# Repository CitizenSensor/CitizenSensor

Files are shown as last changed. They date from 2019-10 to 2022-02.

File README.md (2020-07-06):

# CitizenSensor Nitrate Measurement System

CitizenSensor Nitrate Measurement System

This repository contains all design files for the CitizenSensor nitrate measuring system.

## Repository Layout

```
+ 1_RaspberryPi-HAT/            Raspberry Pi HAT allowing electro-chemical measurements
| + Firmware/                   firmware for the ADuCM350 on the HAT
| + Hardware/                   PCB design files for the HAT
+ 2_Software/                   Main software running on the Raspberry Pi
+ 3_Electrometer/               PCB design files for the electrometer amplifier
+ 4_ConnectorBoard/             PCB design files for a small board to connect further components
+ 5_Enclosure/                  3D printable enclosure
+ 6_Accessories/                Additional helpful items
+ README.md                     this readme
```

## Documentation

Documentation can be found in the [CitizenSensor Wiki](https://github.com/CitizenSensor/CitizenSensor/wiki)

## Known Issues

See [Open Issues](https://github.com/CitizenSensor/CitizenSensor/issues?utf8=%E2%9C%93&q=is%3Aopen+is%3Aissue).

## License

The hardware documentation is licensed under CERN OHL v.1.2.

Software is licensed under GPLv3.

For details see licensing info in the respective sub directories.

---

Copyright FabLab München e.V. and Fraunhofer EMFT 2019-2020

CitizenSensor is sponsored by the Federal Ministry of Education and Research

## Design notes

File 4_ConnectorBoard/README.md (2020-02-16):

# Connector Board

The connector board is a small PCB that sits on top of the CitizenSensor Raspberry Pi HAT and connects additional components to the Raspberry Pi, namely:

* HX711 breakout board to connect the load cell
* KY040 rotary encoder
* Motor for the magnetic stirrer

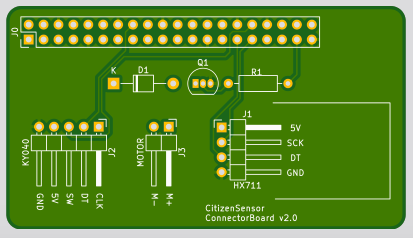
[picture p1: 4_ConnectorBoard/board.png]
PCB


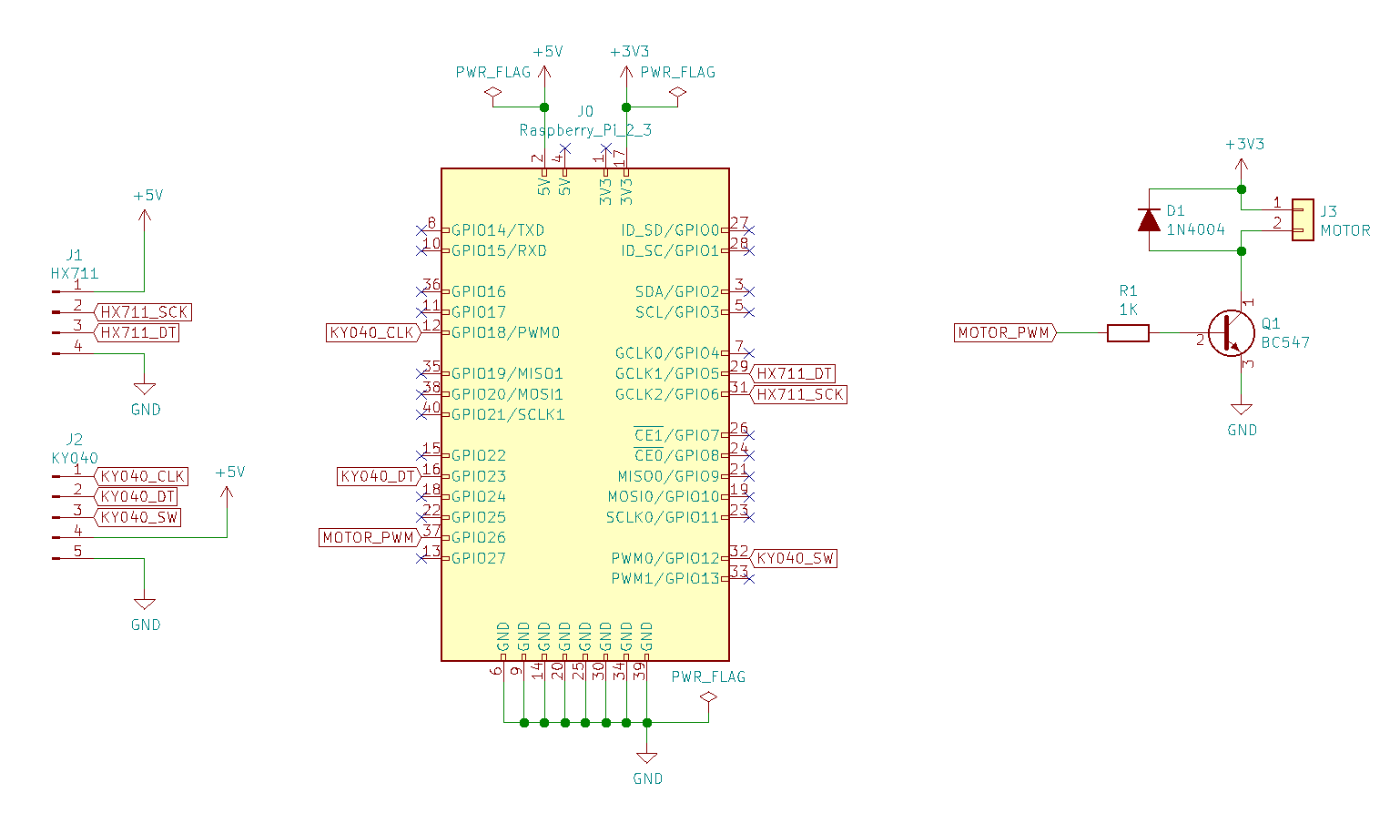
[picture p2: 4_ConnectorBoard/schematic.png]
Schematic


## Bill of Material

| Item | Description | Amount | Comment  |
| --- | --- | ---| ---  |
| J0 | Raspberry Pi Connector | 1 | 40 pins |
| J1 | Pin Header 90° 1x4 | 1 | 2.54 mm raster |
| J2 | Pin Header 90° 1x5 | 1 | 2.54 mm raster |
| J3 | Pin Header 90° 1x2 | 1 | 2.54 mm raster |
| R1 | 1K resistor | 1 | |
| D1 | 1N4004 diode| 1 | |
| Q1 | BC547| 1 | |

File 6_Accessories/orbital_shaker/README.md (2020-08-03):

# CitizenSensor Orbital Shaker

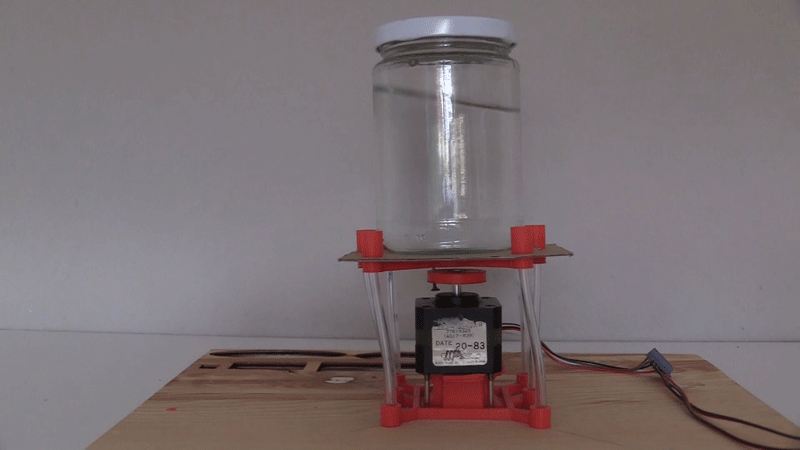
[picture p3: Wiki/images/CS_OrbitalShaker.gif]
CitizenSensor Orbital Shaker


The CitizenSensor Orbital Shaker is an Open Source device for shaking fluids.
This device was designed for for step ["Creation of Aqueous Solution"](https://github.com/CitizenSensor/CitizenSensor/blob/master/Wiki/CS_Usage_AqueousSolution.md), where an aqueous solution
is created by dissolving a soil sample in water. 

The design of the CitizenSensor Orbital Shaker has the following objectives:
- Construction based on few and simple components
- Support of sufficient load capacity (filled jam jar with a total weight of 450g)
- Robust mechanics for mixing the aqueous solution over a time period of 2 hours

## Assembly Instructions

1. Print the 3D Parts P1 - P3 (Recommended print parameters: 3 Shells, Infill 90%)
2. Sand the inner side of the circular ring of part P2 to reduce friction of the rotating nail
3. Place the stepper motor on a wood panel (at least 10 cm x 10 cm) and mark the locations of the holes in the stepper motor.
4. Drill the holes for fastening the stepper motor. Us a drill with a diameter that matches the screws for the stepper motor S1.
5. Place the Orbital Shaker Base P1 on the wood panel and put the Stepper Motor M1 on top.
6. Fasten the stepper motor M1 with the four screws S1.
7. Screw the clamping ring R1 tight on the stepper motor axis
8. Drill a little hole into the Orbital Shaker Rotating Disc - just as big that the thin nail N1 has a tight fits 
9. Mount the Orbital Shaker Rotating Disc on the clamping ring R1
10. Twist the six thin tubes in the holes of the shaker base 
11. Mount the Orbital Shaker Top: twist in the six thin tubes in the holes of the shaker top
12. Place the Orbital Shaker Platform P4 on the Orbital Shaker Top P2.
13. Connect the stepper motor to the stepper motor driver
14. Connect the stepper motor to the 12V power source
15. Connect the Arduino to the 5V power source
The Orbital Shaker Rotating Disc should now move the Orbital Shaker Top.
16. Disconnect the Arduino from the power source
17. Put the jam jar on the Orbital Shaker Platform, then reconnect the Arduino to the power source. The Orbital Shaker should now shake the jam jar.

In case the mechanics does not properly move, re-check that all tubes properly fit in the Orbital Shaker Base and Top. Also the Orbital Shaker Top might need smoe more sanding. 

## Bill of Material

| Item | Description | Amount | Comment  |
| --- | --- | ---| ---  |
| P1 | Orbital Shaker Base | 1 | 3D Print |
| P2 | Orbital Shaker Top | 1 | 3D Print |
| P3 | Orbital Shaker Rotating Disc | 1 | 3D Print |
| P4 | Orbital Shaker Platform | 1 | Lasercut |
| M1 | Stepper Motor | 1 | |
| R1 | Clamping Ring | 1 | Inside diameter must correspond to stepper motor axis |
| S1-S4 | Screws for Stepper Motor | 4 | |
| A1 | Arduino | 1 | |
| C1 | Stepper Motor Driver | 1 | |
| PS1 | Power Supply 12V | 1 | |
| PS2 | Power Supply 5V | 1 | |
| C1 | USB Cable | 1 | |
| T1-T6 | Thin Tube | 6 | Length: 82 mm, Outside Diameter 5mm |
| N1 | Thin Nail | 1 | |

## Credits

The CitizenSensor Orbital Shaker was inspired by the following projects:

* [Hackteria Orbital Shaker](https://www.hackteria.org/wiki/Orbital_Shaker)
* [Open Source Orbital Shaker by jmil (Thingiverse)](https://www.thingiverse.com/thing:5045)
* [DIYbio Orbital Shaker V 1.0 by ProgressTH (Thingiverse)](https://www.thingiverse.com/thing:2633507)
* [Crickit Lab Shaker by Ruiz Brothers (Adafruit)](https://learn.adafruit.com/crickit-lab-shaker/)

## License

Copyright FabLab Muenchen e.V. and Fraunhofer EMFT 2019.

This documentation describes Open Hardware and is licensed under the CERN OHL v. 1.2.

You may redistribute and modify this documentation under the terms of the CERN OHL v.1.2. 
(http://ohwr.org/cernohl). This documentation is distributed WITHOUT ANY EXPRESS OR 
IMPLIED WARRANTY, INCLUDING OF MERCHANTABILITY, SATISFACTORY QUALITY AND FITNESS FOR A 
PARTICULAR PURPOSE. 

Please see the CERN OHL v.1.2 for applicable conditions.

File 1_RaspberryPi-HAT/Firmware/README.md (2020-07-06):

# ADuCM350 Firmware for the Citizensensor project
> Code created by Matthias Steinmaßl

The Pi HAT equippes a M350 from Analog Devices. The Firmware can be compiled using IAR EWARM.

## Functions

It integrates readout of internal ADCs, basic communication functions with UART and BME680 (not tested).

Make sure that in the file `C:\Analog Devices\ADuCM350BBCZ\Eval-ADUCM350EBZ\inc\config\adi_i2c_config.h`
the settings are:
```
#define ADI_I2C_CFG_ENABLE_DMA_SUPPORT                     0
#define ADI_I2C_CFG_SLAVE_MODE_SUPPORT                     0
#define ADI_I2C_CFG_ENABLE_STATIC_CONFIG_SUPPORT           1
#define ADI_I2C_CFG_ENABLE_CALLBACK_SUPPORT                0
```

Open this directory: `C:\Analog Devices\ADuCM350BBCZ\` and clone the CitizenSensor repository here:
`git clone https://github.com/CitizenSensor/CitizenSensor`.

Open `C:\Analog Devices\ADuCM350BBCZ\CitizenSensor\1_RaspberryPi-HAT\Firmware\iar\Chronopotentiometrie.c`
with the IAR EWARM code-size limited IDE ([Link](https://www.iar.com/iar-embedded-workbench/#!?architecture=Arm)) and try to make it.

If it fails, check the following settings:
1. Project-Options-Build Actions: Correct path to ielftool.exe
2. Project-Options-C/C++ Compiler/Preprocessor: Check the correct paths to */examples, */inc and */inc/config
3. Check if all the files in Driver, System and Test Sources can be found, and if not re-add them.

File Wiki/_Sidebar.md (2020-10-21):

Überblick
* [CitizenSensor Überblick](https://github.com/CitizenSensor/CitizenSensor/wiki/Home-DE) 

Dokumentation
* [CitizenSensor Montage](https://github.com/CitizenSensor/CitizenSensor/blob/master/Wiki/CS_Assembly-DE.md)
* [CitizenSensor Bedienung](https://github.com/CitizenSensor/CitizenSensor/blob/master/Wiki/CS_Usage-DE.md)
* [CitizenSensor Gerät](https://github.com/CitizenSensor/CitizenSensor/blob/master/Wiki/CS_Device-DE.md)
* [CitizenSensor Werkzeuge](https://github.com/CitizenSensor/CitizenSensor/wiki/Home-DE)

Hardware 
* [RaspberryPi-HAT](https://github.com/CitizenSensor/CitizenSensor/wiki/Home-DE)
* [Elektrometer](https://github.com/CitizenSensor/CitizenSensor/wiki/Home-DE)
* [Connector Board](https://github.com/CitizenSensor/CitizenSensor/wiki/Home-DE)
* [Enclosure](https://github.com/CitizenSensor/CitizenSensor/wiki/Home-DE)

Software 
* [RaspberryPi Software](https://github.com/CitizenSensor/CitizenSensor/wiki/Home-DE)
* [RaspberryPi-HAT Firmware](https://github.com/CitizenSensor/CitizenSensor/wiki/Home-DE)

Community
* [Messstationen](https://github.com/CitizenSensor/CitizenSensor/wiki/Home-DE)
* [Mitmachen](https://github.com/CitizenSensor/CitizenSensor/wiki/Home-DE)

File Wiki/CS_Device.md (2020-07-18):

[Deutsche Version dieser Seite](https://github.com/CitizenSensor/CitizenSensor/blob/master/Wiki/CS_Device-DE.md)

# CitizenSensor Device #

CitizenSensor Device
_Image 1: CitizenSensor Device_

## Device Functionality ## 

CitizenSensor is a device for electrochemical measurement of nitrate in soil.
The CitizenSensor device can not only carry out nitrate measurements, but also supports the user in all steps necessary to prepare a nitrate measurement.

The CitizenSensor device can also be used to prepare the calibration solutions and ion amplifier solutions required for nitrate measurement.

## Structure of the Device ##

The CitizenSensor device consists of a specially shaped housing and the electronics contained in it for the electrochemical measurement of nitrate.

### Housing Top ###

At the top of the CitizenSensor housing there are several openings in which larger or smaller cups can be placed.

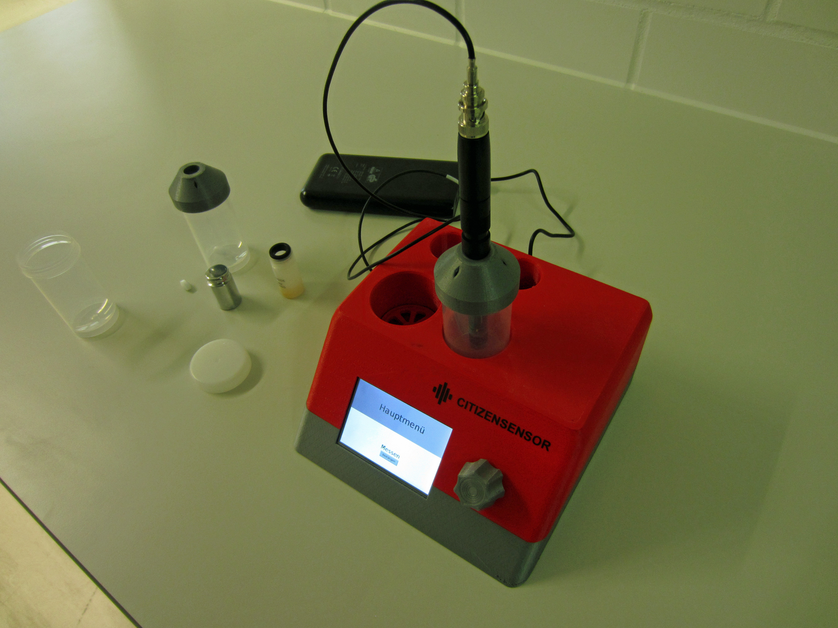
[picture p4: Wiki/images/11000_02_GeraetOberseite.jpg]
CitizenSensor Device Top

_Bild 2: Top of CitizenSensor Device_

The large front openings are intended for placement of cups (200 ml). 

In the bottom of the left front opening there is a scale which is used for weighing in salts, water or soil.  

In the bottom of the right, front opening, a magnetic stirrer is integrated, which supports the preparation of solutions and enables stirring during nitrate measurement.

### Housing Front ###

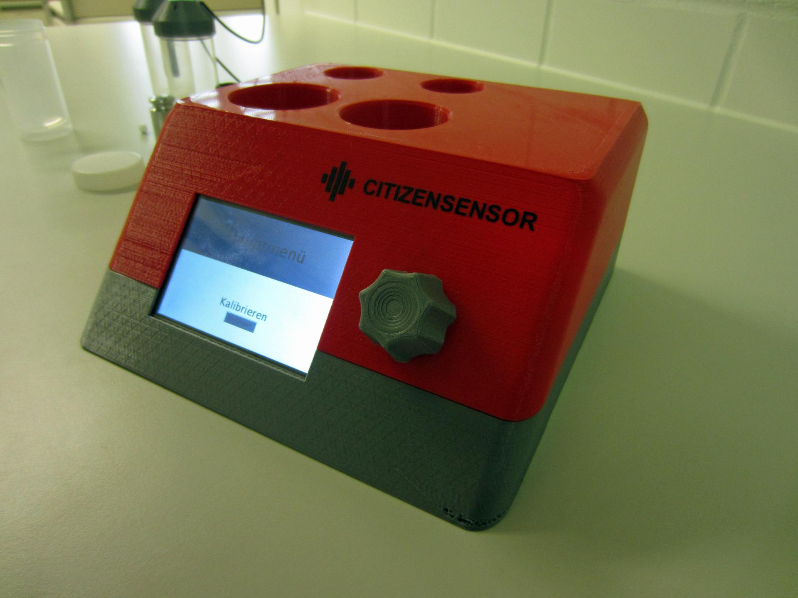
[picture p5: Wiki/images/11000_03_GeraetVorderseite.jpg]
CitizenSensor Device Front

_Image 3: Front of CitizenSensor Device_

For user interaction, the CitizenSensor device has a control button on the front for user input. The control button can be turned to the right, to the left and it can be pressed.

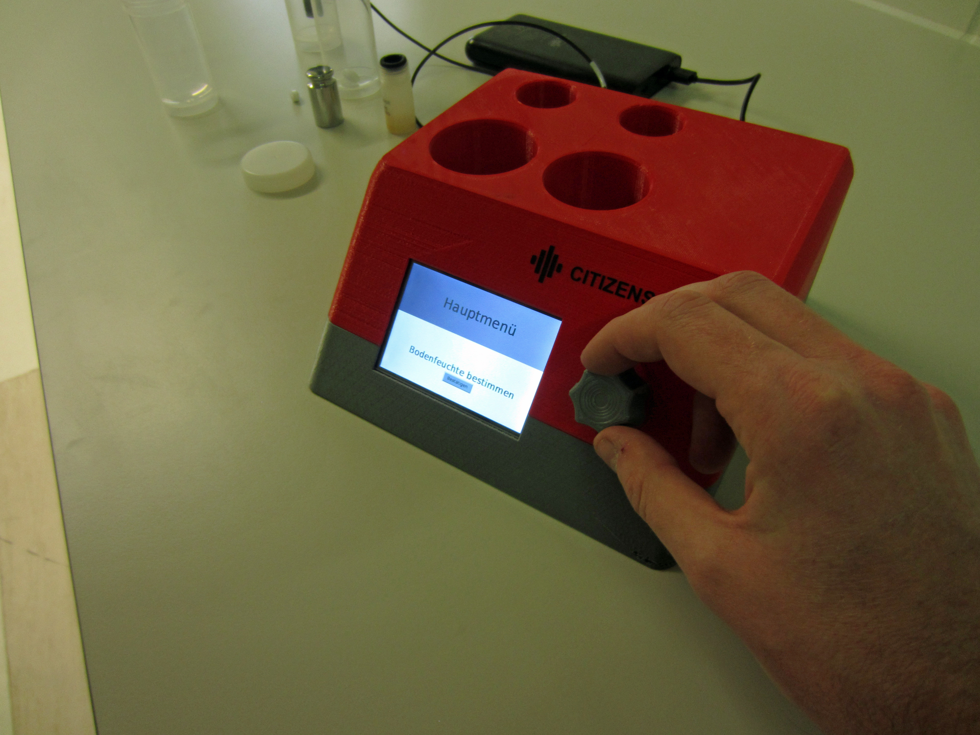
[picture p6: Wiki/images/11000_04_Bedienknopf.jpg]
CitizenSensor Control Button

_Image 4: CitizenSensor Control Button_

The large touch display serves on the one hand for graphic displays of operating steps, but can also be used as an input device for clicking on buttons.

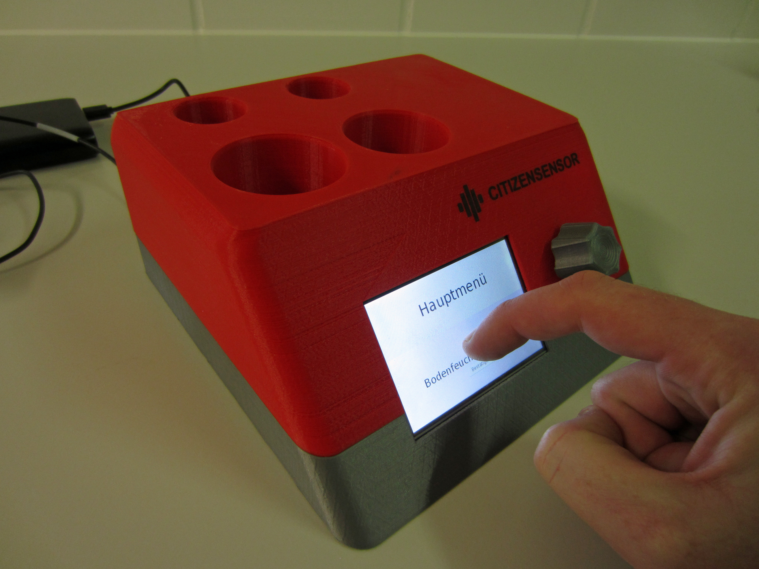
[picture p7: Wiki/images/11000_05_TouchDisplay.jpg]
CitizenSensor Touch Display

_Image 5: CitizenSensor Touch Display_

### Housing Back ###

At the back of the CitizenSensor device there is a Micro-USB socket and a BNC socket.

The CitizenSensor device is supplied with power via the Micro-USB socket. For this purpose a USB charger with 2A should be used.  

An electrochemical sensor can be connected to the BNC socket.

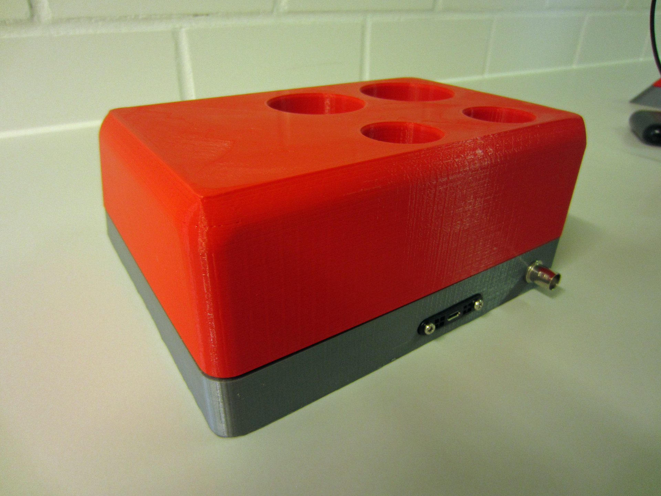
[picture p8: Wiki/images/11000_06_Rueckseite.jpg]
CitizenSensor Back

_Image 6: CitizenSensor Back_

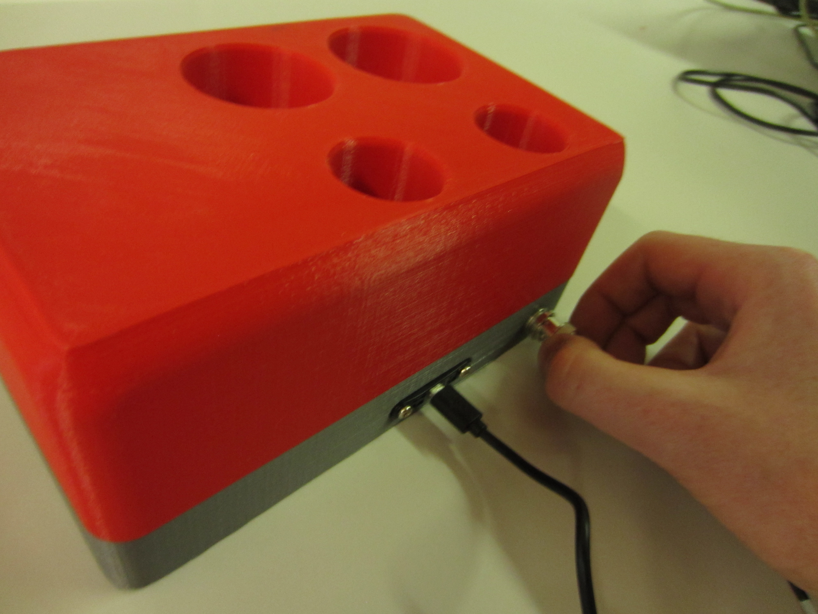
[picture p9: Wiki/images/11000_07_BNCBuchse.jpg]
BNC Socket

_Image 7: BNC Socket_

## Operating the CitizenSensor Device ##

### Startup ###

The unit turns on as soon as it is connected to a power source. At startup, some output is first made on the command line. Then the CitizenSensor welcome screen is displayed, followed by the main menu. It takes about one minute in total until the device has started up and can be operated. Do not disconnect the unit from the power source during start up.

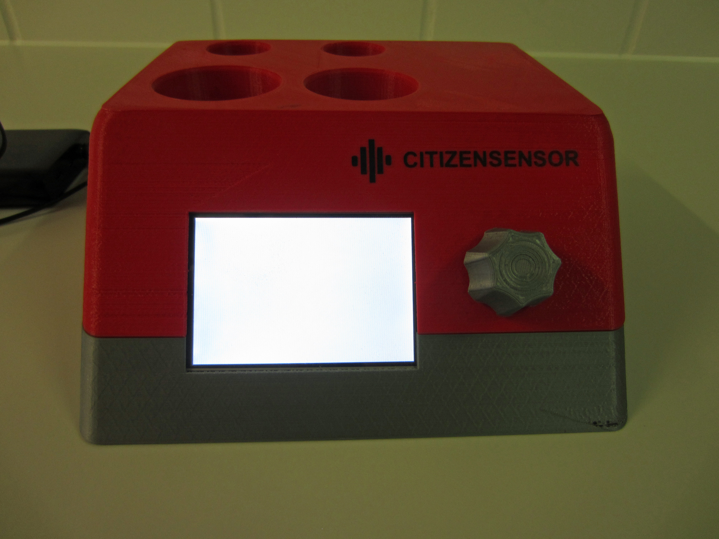
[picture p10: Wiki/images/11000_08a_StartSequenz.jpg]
CitizenSensor Device Power On

_Image 8a: CitizenSensor Device Display on Power On_

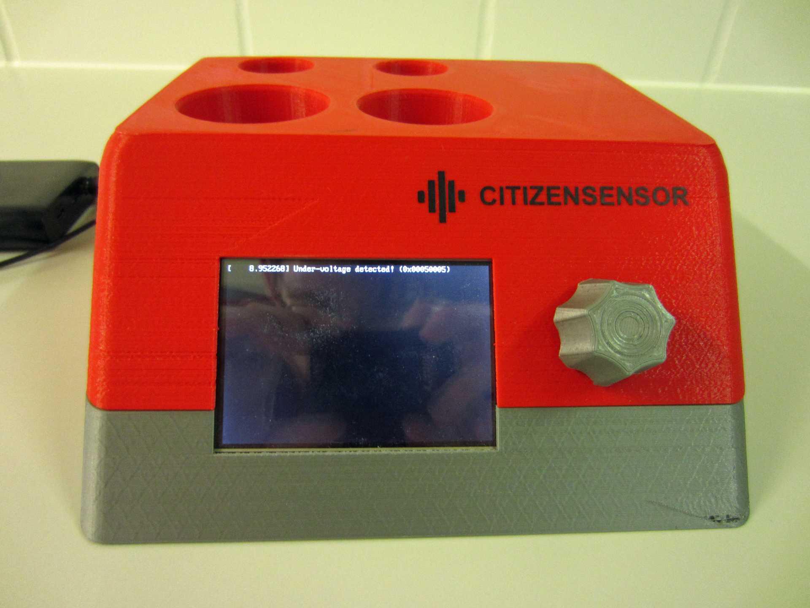
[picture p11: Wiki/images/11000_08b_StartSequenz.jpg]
CitizenSensor Device Startup

_Image 8b: CitizenSensor Device Display on Startup_

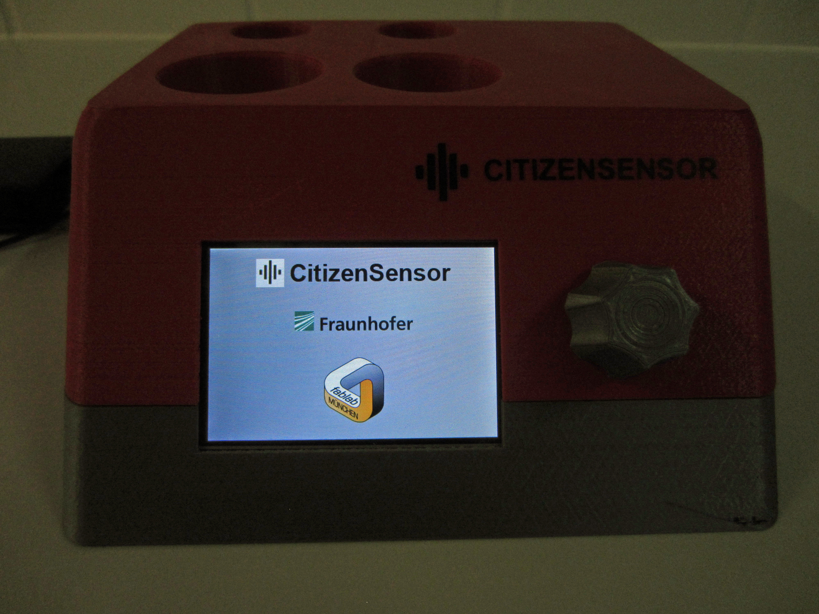
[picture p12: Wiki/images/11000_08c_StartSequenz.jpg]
Started CitizenSensor Device

_Image 8c: Started CitizenSensor Device_

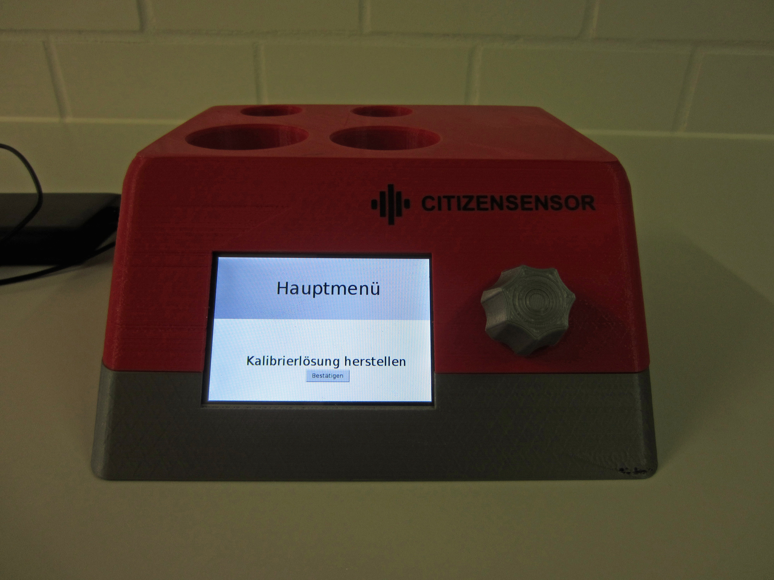
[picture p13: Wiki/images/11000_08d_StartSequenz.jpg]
CitizenSensor Device Menu

_Image 8d: CitizenSensor Device Menu_

### Function Selection ###

After starting, the menu of the CitizenSensor device is displayed. The menu structure of the CitizenSensor device is
- Calibration
- Nitrate measurement
- etc

The current function can be **selected** by **rotating** the control button.

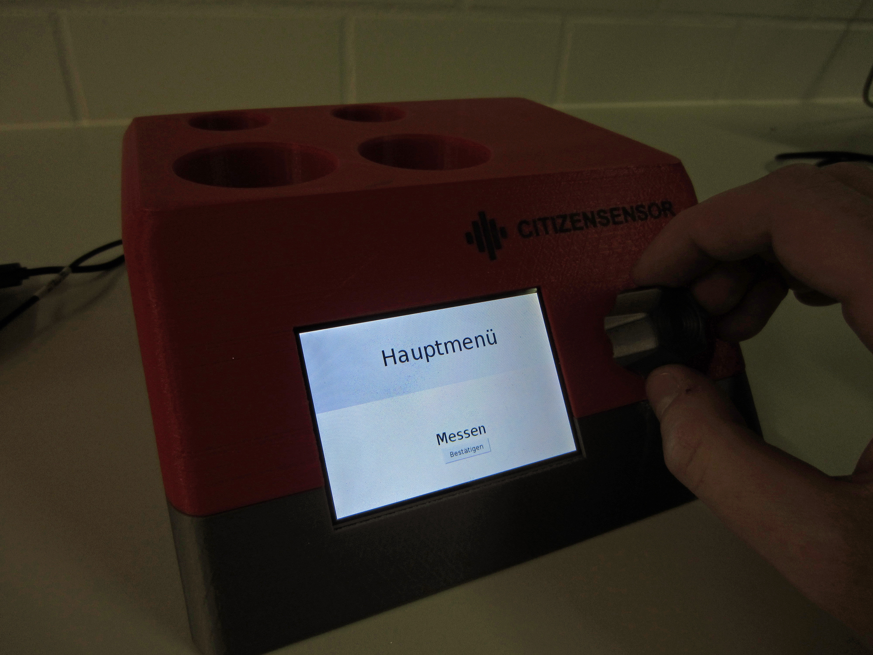
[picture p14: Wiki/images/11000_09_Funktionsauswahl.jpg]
CitizenSensor Function Selection

_Image 9: Selection of CitizenSensor Function "Messen"_

The currently selected function can be **started** by **pressing** the control button.

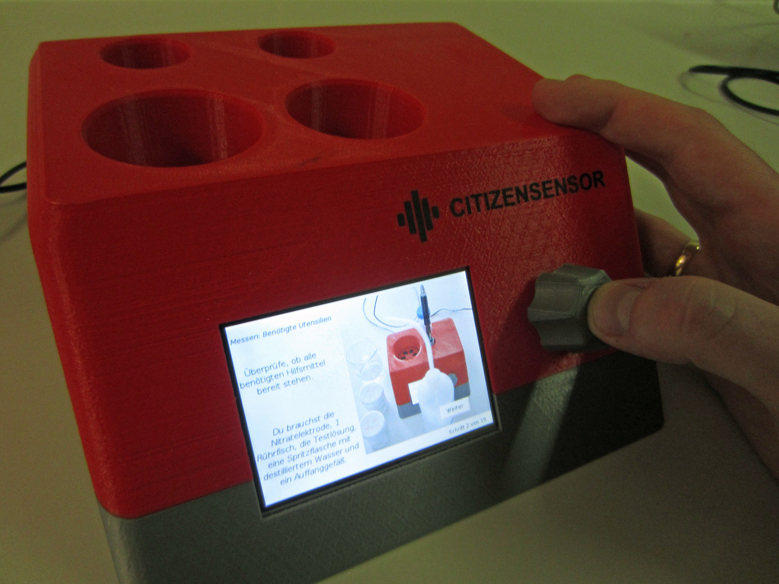
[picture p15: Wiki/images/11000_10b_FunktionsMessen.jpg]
CitizenSensor Function Start

_Image 10b: Start of CitizenSensor Function "Messen"_

After starting a function, the device runs through all steps of the selected function. In the case of the "Calibration" function, for example, these are the steps

- Select calibration solution
- Rinse electrode
- Start stirring the calibration liquid
- Measurement of the calibration liquid

The individual steps of the functions are self-explanatory - all necessary information and instructions are shown on the touch display.

After the last step of a function, the device returns to the main menu.

### Switch Off ###

The CitizenSensor device can be switched off by selecting the "Herunterfahren" function.

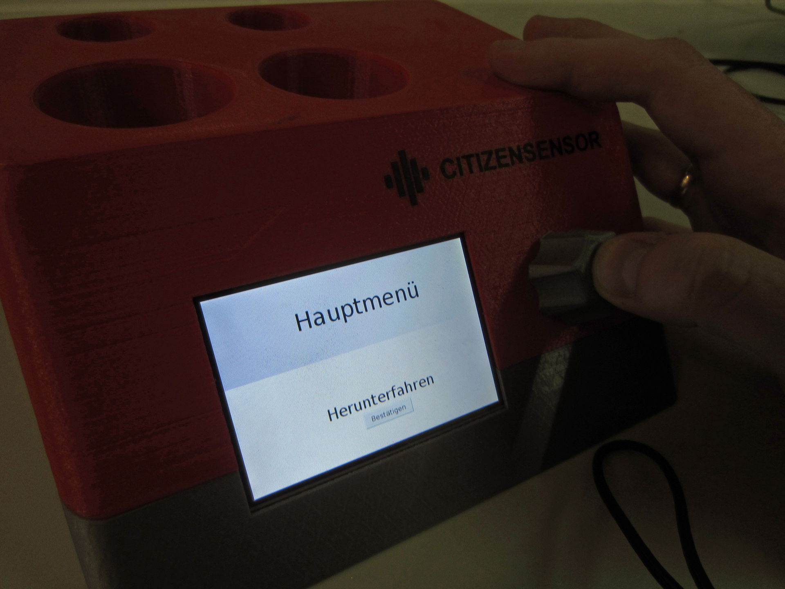
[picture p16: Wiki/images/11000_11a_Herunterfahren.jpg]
CitizenSensor Switch Off

_Image 11a: CitizenSensor Switch Off_

The switch-off process takes about 15 seconds. After selecting "Herunterfahren", the unit will shut down. Once the screen is black, the CitizenSensor device can be disconnected from the power source.

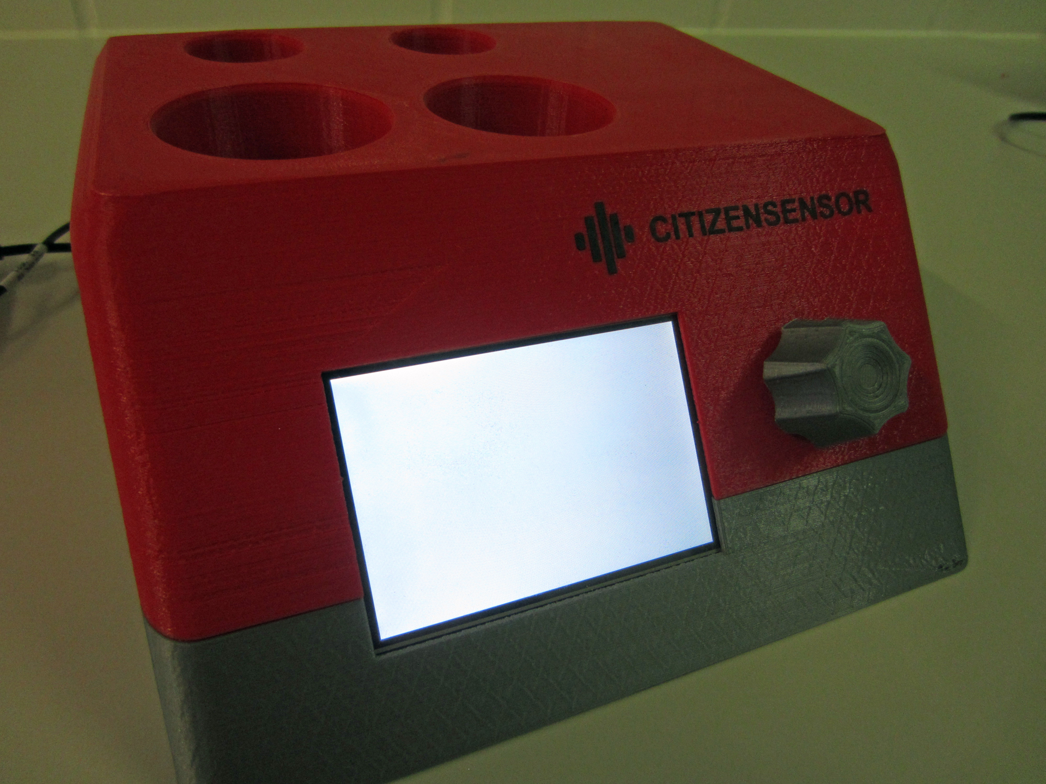
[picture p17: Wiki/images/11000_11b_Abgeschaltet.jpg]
CitizenSensor Switched Off

_Bild 11b: Switched Off CitizenSensor Device_

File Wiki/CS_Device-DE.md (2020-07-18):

[English version of this page](https://github.com/CitizenSensor/CitizenSensor/blob/master/Wiki/CS_Device.md)

# CitizenSensor Gerät #

CitizenSensor Gerät
_Bild 1: CitizenSensor Gerät_

## Funktionen des Geräts ## 

CitizenSensor ist ein Gerät zur elektrochemischen Messung von Nitrat im Boden.
Das CitizenSensor Gerät kann nicht nur Nitratmessungen durchführen, sondern unterstützt den Benutzer auch bei allen Schritten, die für die Vorbereitung einer Nitratmessung erforderlich sind.

So können mit dem CitizenSensor Gerät auch die für die Nitratmessung benötigten Kalibrier- und Ionenverstärker-Lösungen hergestellt werden.

## Aufbau des Geräts ##

Das CitizenSensor Gerät besteht aus einem speziell geformten Gehäuse, sowie der darin enthaltenen Elektronik für die elektrochemische Messung von Nitrat.

### Oberseite ###

An der Oberseite des CitizenSensor Gehäuses  befinden sich mehrere Öffnungen, in die  größere oder kleinere Becher eingestellt werden können.

CitizenSensor Gerät Oberseite
_Bild 2: Oberseite des CitizenSensor Geräts_

Die großen vorderen Öffnungen sind für das Einstellen von Bechern (200 ml) vorgesehen. 

Im Boden der linken, vorderen Öffnung befindet sich eine Waage, die beim Einwiegen von Salzen, Wasser oder Erde zum Einsatz kommt.  

Im Boden der rechten, vorderen Öffnung, ist ein Magnetrührer integriert, der bei der Herstellung von Lösungen unterstützt, sowie das Rühren während der Nitratmessung ermöglicht.

### Vorderseite ###

CitizenSensor Gerät Vorderseite
_Bild 3: Vorderseite des CitizenSensor Geräts_

Für den Dialog mit dem Benutzer besitzt das CitizenSensor Gerät an der Vorderseite einen Bedienknopf für Benutzereingaben. Der Bedienknopf kann nach rechts oder links gedreht, sowie gedrückt werden.

CitizenSensor Gerät Bedienknopf
_Bild 4: Bedienknopf des CitizenSensor Geräts_

Das große Touch-Display dient einerseits für  grafische Anzeigen von Bedienungsschritten, kann andererseits aber auch als Eingabegerät für den Klick auf Buttons genutzt werden.

CitizenSensor Gerät Touch-Display
_Bild 5: Touch-Display des CitizenSensor Geräts_

### Rückseite ###

An der Rückseite des CitizenSensor Geräts befinden sich eine Micro-USB Buchse, sowie eine BNC-Buchse.

Über die Micro-USB Buchse wird das CitizenSensor Gerät mit Strom versorgt. Dafür sollte ein USB-Ladegerät mit 2A eingesetzt werden.  

An der BNC-Buchse kann ein elektrochemischer Sensor angeschlossen werden.

CitizenSensor Gerät Rückseite
_Bild 6: Rückseite des CitizenSensor Geräts_

CitizenSensor Gerät BNC-Buchse
_Bild 7: BNC-Buchse des CitizenSensor Geräts_

## Bedienung des Geräts ##

### Einschalten ###

Das Gerät schaltet sich ein, sobald es an einen Stromquelle angeschlossen wird. Beim Start erfolgen zunächst einige Ausgaben auf der Kommandozeile. Anschließend wird der CitizenSensor Begrüßungsbildschirm dargestellt, gefolgt von der Darstellung des Hauptmenüs. Es dauert insgesamt etwa eine Minute bis das Gerät hochgefahren ist und bedient werden kann. Während des Hochfahrens sollte das Gerät nicht von der Stromquelle getrennt werden.

CitizenSensor Gerät Einschalten
_Bild 8a: Display des CitizenSensor Geräts beim Einschalten_

CitizenSensor Gerät Start
_Bild 8b: Display des CitizenSensor Geräts während dem Start_

CitizenSensor Gerät Gestartet
_Bild 8c: Display des CitizenSensor Geräts nach dem Start_

CitizenSensor Gerät Menü
_Bild 8d: Menü des CitizenSensor Geräts nach dem Start_

### Funktionsauswahl ###

Nach dem Start wird das Menü des CitizenSensor Geräts angezeigt. Die Menüstruktur des CitizenSensor Geräts ist
- Kalibrieren
- Nitratmessung
- usw

Die aktuelle Funktion kann durch **Drehen** des Dreh/Druckknopfes **gewählt** werden.

CitizenSensor Funktionsauswahl
_Bild 9: Auswahl der CitizenSensor Funktion "Messen"_

Die aktuell gewählte Funktion kann durch **Drücken** des Dreh/Druckknopfes **gestartet** werden.

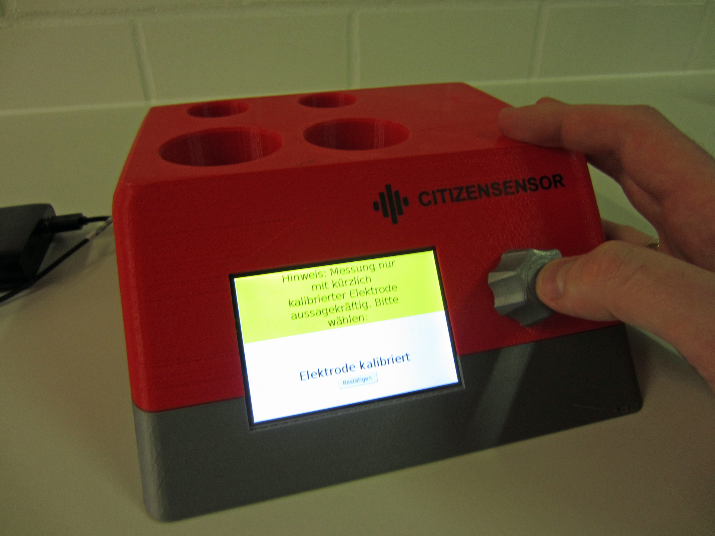
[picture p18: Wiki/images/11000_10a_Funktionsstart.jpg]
CitizenSensor Funktionsbestätigung

_Bild 10a: Bestätigung der CitizenSensor Funktion "Messen"_

Die Funktion "Messen" erfordert eine weitere Bestätigung durch den Bediener. Durch nochmaliges **Drücken** des Dreh/Druckknopfes wird die Funktion "Messen" **gestartet**.

CitizenSensor Funktion Start
_Bild 10b: CitizenSensor Funktion "Messen" starten_

Nach dem Start einer Funktion, durchläuft das Gerät alle Schritte der gewählten Funktion. Im Fall der Funktion "Kalibrieren" sind das zum Beispiel die Schritte

- Kalibrierlösung wählen
- Elektrode spülen
- Rühren der Kalibrierflüssigkeit starten
- Messung der Kalibrierflüssigkeit

Die einzelnen Schritte der Funktionen sind selbsterklärend - alle benötigten Informationen und Hinweise werden auf dem Touch-Display angezeigt.

Nach dem letzten Schritt einer Funktion kehrt das Gerät in das Hauptmenü zurück.

### Ausschalten ###

Das CitizenSensor Gerät kann durch Auswahl der Funktion "Herunterfahren" ausgeschaltet werden.

CitizenSensor Herunterfahren
_Bild 11a: Ausschalten des CitizenSensor Geräts_

Der Ausschaltvorgang dauert etwa 15 Sekunden. Nach der Auswahl von "Herunterfahren" fährt das Gerät herunter. Sobald der Bildschirm schwarz ist, kann das CitizenSensor Gerät von der Stromquelle getrennt werden.

CitizenSensor Ausgeschaltet
_Bild 11b: Ausgeschaltetes CitizenSensor Gerät_

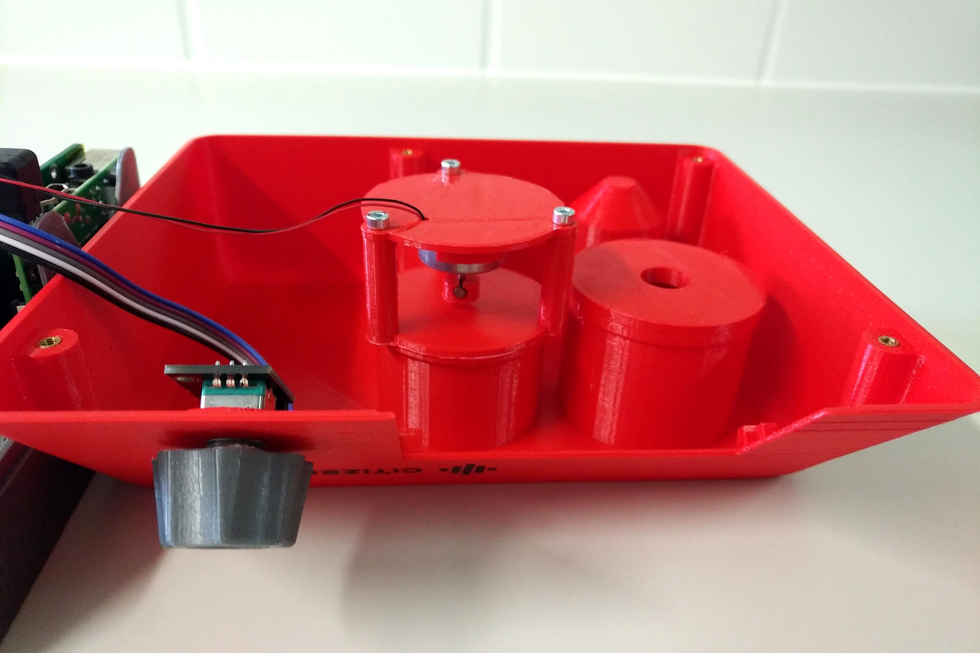
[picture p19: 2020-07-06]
Wiki/images/11000_GerätOffen3.jpg

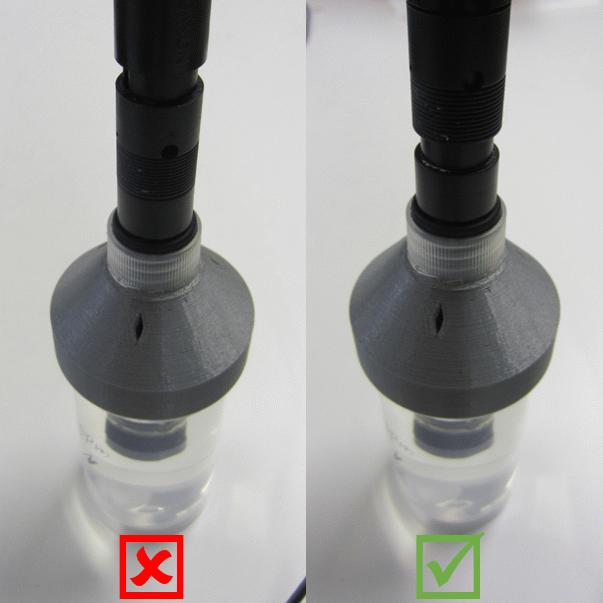
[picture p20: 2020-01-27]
2_Software/photos/ringzu.gif

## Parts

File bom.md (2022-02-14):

# Bill of Material

| Item                             | Amount | Article number                | Comment                            |
|----------------------------------|--------|-------------------------------|------------------------------------|
| Raspberry Pi                     | 1      | we used a 3 B+                |                                    |
| MicroSD card 16GB                | 1      |                               |                                    |
| CitizenSensor Raspi HAT          | 1      | see folder 1\_RaspberryPi-HAT |                                    |
| CitizenSensor electrometer board | 1      | see folder 3\_Electrometer    |                                    |
| CitizenSensor connector board    | 1      | see folder 4\_ConnectorBoard  |                                    |
| Load cell 100g                   | 1      | Sparkfun TAL221               |                                    |
| HX711 breakout board             | 1      |                               |                                    |
| KY-040 rotary encoder            | 1      |                               |                                    |
| USB 90° adapter                  | 1      | Reichelt DELOCK 65668         |                                    |
| USB socket with cable            | 1      | Reichelt DELOCK 85245         |                                    |
| Display                          | 1      | Reichelt RASP PI 3.5TD        |                                    |
| Ribbon cable 26-way              | 1      | Reichelt AWG 28-26G 3M        |                                    |
| Socket 2x20                      | 1      | Reichelt PFL 40               |                                    |
| Connector 2x13                   | 1      | Reichelt WSL 26SK             |                                    |
| BNC jack                         | 1      | Pollin 94-450423              |                                    |
| Raspi power supply               | 1      | Reichelt RASP NT 25 SW E      |                                    |
| Enclosure                        | 1      | 3d printed                    | All parts from folder 5\_Enclosure |
| Screw M2.5x5                     | 4      |                               | for mounting Raspi                 |
| Screw M3x10                      | 6      |                               | enclosure and load cell            |
| Screw M3x20                      | 2      |                               | load cell                          |
| Brass insert nuts M3             | 8      |                               |                                    |
| Brass insert nuts M2.5           | 2      |                               |                                    |
| Nitrate electrode                | 1      | Conatex Pasco 1184013         | https://www.pasco.com/products/sensors/environmental/ps-3521 |
| Magnet for stirrer               | 2      | Reichelt MAGNET 3.4           | Diameter 3mm, Length 4mm           |
| Motor for stirrer                | 1      | Reichelt SOLAR 90002L         |                                    |

# Accessories

| Item                             | Amount | Article number                | Comment                            |
|----------------------------------|--------|-------------------------------|------------------------------------|
| Power supply, USB micro          | 1      | 5v, 2.5A                      |                                    |
| Magnetic stir bar                | 1      | behr-labor.de 6231865         | oval, 15x6mm                       |
| Plastic cup with screw cap       | 5      | https://www.ebay.de/itm/114186153530 or https://www.ebay.de/itm/263547305540  | 100ml, Diameter 43mm, TWIN dispatch containers       |
| Screw cap with hole for electrode | 1     | see folder 6\_Accessories     | 3d printed                         |
| 100g calibration weight          | 1      | e.g. https://www.ebay.de/itm/140864008419  |                            |

# Consumables
| Item                             | Amount | Article number                | Comment                            |
|----------------------------------|--------|-------------------------------|------------------------------------|
| Ammoniumsulfate                  | 250g   | https://www.ebay.de/itm/263173160589||
| Kaliumnitrat                     | 1 kg   | https://www.restauro-online.com/Kaliumnitrat-rein-KNO3-Kalisalpeter||

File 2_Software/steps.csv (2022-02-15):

ID | Process step |  | User Action Required |  | Changing process parameter |  | End-point detection |  |  | Precautions/Conditions |  | Image
<ID> | Process step | <group> | <y/n> | <Description> | <Name> | <Measurement method> | <y/n> | <Description> | <Estimated Time> | <Short Desc> | <Long Description>
100 | Cleaning | Cleaning | y | In a beaker, carefully pour distilled water on the electrode
101 | Connect Board | Connection | y | Plug the board into the connector | GPIO | GPIO | y | GPIO | 30 | Not plugged in | No other sensor board should be plugged in
102 | Fill in acid | preparation | y | Fill in H2PO4 solution | Filling level | ? | y | TRUE/FALSE | 30 | - | -
103 | Perform CV | Analyse | n | perform CV until CV is stable | CV curve | CV | y | CV | 900 | - | -
104 | Rinsing | Cleaning | y | Pour out acid, rinse with water | Conductivity | Impedance analysis | y | Filling level | 60 | - | -
199 | Switch on PalmSens | Measurement | y | Press Power button on PalmSens | - | - | - | - | - | - | - | power.gif
200 | Potassiumhexacyanidoferrate | Measurement
201 | Power Palmsens | Measurement | y | Connect the PalmSens to a power supply with the given power adapter | - | - | - | - | - | Handle with care | The PalmSens sided connecter should be inserted with care. | palmsens.gif
202 | deoxygeneate solution with Nitrogen | Measurement |  | put the tube connected to Nitrogen pump into solution and open valve |  |  |  |  | 20 |  |  | degasify.gif
203 | Connect PalmSens USB | connection | y | Connect the PalmSens to the PC/Laptop with a USB-RS232 Cable. | usb port access | checks idvendor and idproduct of cable rs232 | - | - | - | Don't forget adapter | Ensure that the gender changer and the null modem are connected on PalmSens side. | usb_new.gif
204 | Start PSTrace Software | Measurement | n | Click on PSTrace to start PSTrace software | New Task is created in Windows | Check Tasks with Python | - | - | - | - | - | pstrace.gif
205 | Connect Software to PalmSens | Measurement | y | chooses COM Port | - | - | - | - | - | - | - | connect.gif
206 | Load CV method |  |  | load saved method using pstrace interface |  |  |  |  |  |  |  | palmsens.gif
207 | Set right values |  |  |  |  |  |  |  |  |  |  | palmsens.gif
208 | connect Sensor cable to Palmsens |  |  |  |  |  |  |  |  |  |  | montage.gif
209 | Reference electrode connection | connection |  | connect RE cable (blue) to commercial reference electrode using a clamp |  |  |  |  |  |  |  | power1.gif
210 | Working electrode connection |  |  | connect WE cable (red) to red connector of breakoutboard |  |  |  |  |  |  |  | usb1.gif
211 | Counter electrode connection |  |  | connect CE cable (black) to black connector of breakoutboard |  |  |  |  |  |  |  | usb1.gif
212 | sensor board connection |  |  | plug sensor into board |  |  |  |  |  |  |  | usb1.gif
213 | take the laboratory stand and put upper clamp really high | montage |  |  |  |  |  |  |  |  |  | usb1.gif
214 | Mount breaktouboard to upper clamp of laboratory stand | montage |  |  |  |  |  |  |  |  |  | usb1.gif
215 | Mount container with potassiumhexacyanidoferrat to lower clamp of laboratory stand | montage |  |  |  |  |  |  |  |  |  | usb1.gif
216 | Change height of upper clamp, that sensor dips in solution | montage |  |  |  |  |  |  |  |  |  | usb1.gif
217 | Start measurement |  |  |  |  |  |  |  |  |  |  | usb1.gif
218 | Prepare potassiumhexacyanidoferrat solution | Measurement |  | pour potassiumhexacyanidoferrat in water |  |  |  |  |  |  |  | usb1.gif
219 | Deoxygeneate solution with stickstoff |  |  |  |  |  |  |  |  |  |  | usb1.gif
220 | step probe | try | y | probe | probe works | result | n | stdout | 30 | try to create step | only give id number and all info will be extracted | usb1.gif
221 | Plot data | Analyse | y | Enter name of data file you would like to plot |  |  | n |  | 0 | only csv files | csv files need to be converted to UTF8 format before submission
222 | Create PalmSens method | Measurement | y | Enter wished parameters of the method |  |  | n |  |  |  |  | methood.gif
300 | Network-IP-Info
301 |  | networkinfo | y |  | info |  | y | info | 10
400 | Hauptmenü
401 |  | mainmenu | y |  | mainmenu |  | y | mainmenu | 10
402 | splash | splash | y |  | splash |  | y | splash | 10 |  |  | splash.png
500 | Kalibrierlösung erstellen
5001 | Abfrage ISA vorhanden |  |  |  |  |  |  |  | 10 |  | Hinweis: Zur Herstellung ist die ISA Lösung notwendig. Bitte wählen:
501 | Becher auf die Waage stellen | calibration | y | Becher auf die Waage stellen | scale | 4g | y | scale | 10 | Stelle einen Becher auf die Waage | Achte darauf, dass der Becher leer und sauber ist. Stelle ihn in die linke Vertiefung (Waage). | becher_waage.gif
5010 | Benötigte Utensilien |  |  |  |  |  |  |  | 10 | Überprüfe, ob folgende Utensilien bereit stehen. | 500 ml Spritzflasche mit destilliertem Wasser, 2 M ISA-Lösung, mind. 3 g Kaliumnitrat, 1 Plastikbecher, 1 Rührfisch, 2 verschließbare Becher, 1 Rührstab, 1 Pipette, 1 Messer, 100g Gewicht | kalibrierlösung_utensilien.gif
502 | Gewünschte Konzentration einstellen | calibration | n |  |  |  | y | KY010 press | 10 | Wähle die gewünschte Nitratkonzentration aus | Scrolle mithilfe des Knopfes durch die möglichen Werte und bestätige mit einem Knopfdruck.
5030 | Waage kalibrieren | calibration | y | Waage kalibrieren | scale | calculated | y | scale | 30 | Kalibriere mit dem 100g Gewicht | Stelle das 100g Gewicht auf die Waage und warte, bis die Kalibrierung abgeschlossen ist. Danach wirst du aufgefordert, das Gewicht wieder zu entfernen. | gewicht_demo.gif
503 | Salz abwiegen | calibration | y | Salz abwiegen | scale | calculated | y | scale | 40 | Wiege das Kaliumnitrat-Salz ab | Benutze einen kleinen Löffel und fang mit wenig an. Eine Messerspitz sind ca. 100 -500 mg. | salz_abwiegen.gif
504 | Fülle Wasser ein | calibration | y | Wasser einfüllen | scale | calculated | y | scale | 30 | Fülle Wasser ein | Fülle möglichst exakt die angegebene Menge Wasser in den Becher ein. | gießen_demo.gif
505 | Becher beschriften | calibration | y | Becher beschriften | scale | -30g +30g | y | scale | 50 | Beschrifte den Becher | Der angegebene Wert entspricht der Konzentration, die du tatsächlich hergestellt hast. Stelle den Becher anschließend in die rechte Vertiefung (Magnetrührer). | beschriften.gif
5060 | Rührfisch einwerfen |  |  |  |  |  |  |  | 10 | Gib den Rührfischer in den Becher | Stelle sicher, dass der Becher im rechten Slot (Magnetrührer) steht. Der Elektromotor wird mit ihm rühren | rührfisch.gif
506 | Rühren | calibration | y | Rühren | scale | -30g +30g | y | scale | 600 | Lass den Magnetrührer arbeiten. Du kannst die Drehgeschwindigkeit durch Drehen einstellen. | Warte, bis keine Salzkristalle mehr sichtbar sind oder der Countdown abgelaufen ist. | becher_demo.gif
5061 | Rührfisch rausholen |  |  |  |  |  |  |  | 10 | Hole den magnetischen Rührfisch wieder raus. | Benutze ein Messer oder eine Pinzette aus Metall, das magnetisch ist (Eisen). | rührfisch_raus.gif
5062 | Verschließen und Schütteln |  |  |  |  |  |  |  | 10 | Verschließe den Becher mit einem Deckel. | Schüttel den Becher anschließend kräftig durch. | beschriften.gif
507 | Neuen verschließbaren Becher auf die Waage stellen |  |  |  |  |  |  |  | 10 | Nimm den vorigen Becher beiseite und stelle einen neuen sauberen Becher auf die Waage. | Achte darauf, dass der Becher mittig auf der Waage steht. | becher_waage.gif
508 | Stammlösung einfüllen |  |  |  |  |  |  |  | 10 | Fülle die Stammlösung, wie angegeben ein. | Benutze dazu die Pipette. Ein Tropfen wiegt bis zu 0.05g. | pipettieren.gif
509 | Fülle Wasser ein | calibration | y | Wasser einfüllen | scale | calculated | y | scale | 30 | Fülle Wasser ein | Fülle möglichst exakt die angegebene Menge Wasser in den Becher ein. | gießen_demo.gif
510 | Becher beschriften | calibration | y | Becher beschriften | scale | -30g +30g | y | scale | 50 | Beschrifte den Becher | Der angegebene Wert entspricht der Konzentration, die du tatsächlich hergestellt hast. Stelle den Becher anschließend wieder auf die Waage. | beschriften.gif
598 | Kalibrierung setzen |  |  |  |  |  |  |  | 5
599 | Reset done |  |  |  |  |  |  |  | 5 | Die Kalibrierdaten wurden durch den gewünschten Wert ersetzt
601 | Sensor spülen | Measurement | y | Sensor spülen | measure | rauschen | n |  | 60 | Spüle den Sensor | Nimm eine Flasche VE Wasser zur Hand und Spüle den Sensor kräftig ab. | spülen.gif
602 | Sensor: Ring öffnen | Measurement | y | Sensor: Ring öffnen | measure | rauschen | n |  | 60 | Öffne den Verschlussring | Schiebe den Verschlussring oben an der Elektrode nach unten. | ringauf.gif
603 | Sensor: Ring schließen | Measurement | y | Sensor: Ring schließen | measure | rauschen | n |  | 60 | Schließe den Verschlussring | Schiebe den Verschlussring oben an der Elektrode zurück nach oben. | ringzu.gif
604 | Elektrode vorbereiten |  |  |  |  |  |  |  | 15 | Falls sich die Elektrode in der Lagerflüssigkeit befand, muss sie jetzt zwei Stunden in die 4ppm- Kalibrierlösung getaucht werden. | Verwende dazu den grauen Deckel und spüle sie vorher mit destilliertem Wasser ab. Andernfalls kannst du sie sofort verwenden.
605 | Elektrode kurzfristig einlagern |  |  |  |  |  |  |  | 15 | Willst du die Elektrode innerhalb der nächsten drei Tage verwenden, dann lagere sie in die 4ppm- Kalibrierlösung ein | Verwende dazu den grauen Deckel und spüle sie vorher mit destilliertem Wasser ab. | eintauchen.gif
606 | Elektrode langfristig einlagern |  |  |  |  |  |  |  | 15 | Willst du die Elektrode nicht innerhalb der nächsten drei Tage verwenden, dann lagere sie in die Lagerflüssigkeit ein | Verwende die zugehörige Lagerflüssigkeit (kleiner Behälter, siehe Bild) | einlagern.gif
700 | Messe: Messung
7001 | Abfrage Kalibrierung |  |  |  |  |  |  |  | 10 |  | Hinweis: Messung nur mit kürzlich kalibrierter Elektrode aussagekräftig. Bitte wählen:
701 | Benötigte Utensilien |  |  |  |  |  |  |  | 10 | Überprüfe, ob alle benötigten Hilfsmittel bereit stehen. | Du brauchst die Nitratelektrode, 1 Rührfisch, die Testlösung, eine Spritzflasche mit destilliertem Wasser und ein Auffanggefäß. | kalibrieren_utensilien.gif
702 | Testflüssigkeit vorbereiten |  |  |  |  |  |  |  | 10 | Stelle die Testflüssigkeit in den linken Slot (Waage). | Stelle sicher, dass der Deckel geöffnet ist. | becher_waage.gif
7020 | Testflüssigkeit vorbereiten |  |  |  |  |  |  |  | 10 | Stelle die Testflüssigkeit in den rechten Slot (Magnetrührer). |  | becher_demo.gif
7021 | Deckel aufschrauben |  |  |  |  |  |  |  | 10 | Nimm den grauen Deckel und schraube ihn auf | Der graue Deckel hat eine Öffnung zur Halterung der Nitratelektrode | deckel.gif
703 | Nitratelektrode vorbereiten |  |  |  |  |  |  |  | 20 | Nimm die Nitratelektrode aus der Lagerflüssigkeit und spüle sie ab. | Benutze destilliertes Wasser und spüle kräftig ca. 10 Sekunden. | abspülen.gif
704 | Nitratelektrode eintauchen |  |  |  |  |  |  |  | 5 | Tauche nun die Elektrode in die Testflüssigkeit ein. | Gib auf die Membran Acht, die sich unten an der Elektrode befindet. Sie sollte keinen Kontakt zum Gefäßboden bekommen. | eintauchen.gif
705 | Messwertanzeige |  |  |  |  |  |  |  | 60 | Nitratmesswert: | Laufende Messwertanzeige im Graph in mV. | eintauchen.gif
7050 | Interpretation Messwert |  |  |  |  |  |  |  | 10 | Aus dem Messwert ergibt sich eine Stickstoffkonzentration von (1 g/m^2 entspricht Nitratkonz. von 10 ppm): |  | qr.gif
706 | Nitratelektrode einlagern |  |  |  |  |  |  |  | 10 | Lagere die Nitratelektrode wieder ein. | Benutze dafür die Lagerungslösung (Üblicherweise 100 ppm NO3-N). | einlagern.gif
800 | Messe:Kalibrierung
801 | Benötigte Utensilien |  |  |  |  |  |  |  | 10 | Überprüfe, ob alle benötigten Utensilien bereit stehen. | Du brauchst die Nitratelektrode, 1 Rührfisch, die beiden Kalibrierlösungen (100 und 4 ppm NO3-N), eine Spritzflasche mit destilliertem Wasser und ein Auffanggefäß. | kalibrieren_utensilien.gif
8015 | Testflüssigkeit vorbereiten |  |  |  |  |  |  |  | 10 | Stelle die Testflüssigkeit mit ca. 100 ppm in den rechten Slot. | Stelle sicher, dass der Deckel geöffnet ist. | becher_demo.gif
802 | Nitratelektrode vorbereiten |  |  |  |  |  |  |  | 20 | Nimm die Nitratelektrode aus der Lagerflüssigkeit und spüle sie ab. | Benutze destilliertes Wasser und spüle kräftig ca. 10 Sekunden | abspülen.gif
803 | Erster Kalibrierpunkt |  |  |  |  |  |  |  | 10 | Tauche die Elektrode in die Kalibrierlösung mit ca. 100 ppm NO3-N | Führe diesen Schritt aus, bis sich der Messwert stabilisiert hat und drücke dann den Button. | eintauchen.gif
8035 | Testflüssigkeit vorbereiten |  |  |  |  |  |  |  | 10 | Stelle die Testflüssigkeit mit ca. 4 ppm in den rechten Slot. | Stelle sicher, dass der Deckel geöffnet ist. | becher_demo.gif
804 | Nitratelektrode spülen |  |  |  |  |  |  |  | 20 | Spüle die Nitratelektrode kräftig mit destilliertem Wasser ab. | Halte sie dafür über das Auffanggefäß und spüle ca. 10 Sekunden | abspülen.gif
805 | Zweiter Kalibrierpunkt |  |  |  |  |  |  |  | 10 | Tauche die Elektrode in die Kalibrierlösung mit ca. 4 ppm NO3-N | Führe diesen Schritt aus, bis sich der Messwert stabilisiert hat und drücke dann den Button. | eintauchen.gif
806 | Nitratelektrode spülen |  |  |  |  |  |  |  | 20 | Spüle die Nitratelektrode kräftig mit destilliertem Wasser ab. | Halte sie dafür über das Auffanggefäß und spüle ca. 10 Sekunden | abspülen.gif
807 | Nitratelektrode einlagern |  |  |  |  |  |  |  | 10 | Lagere die Nitratelektrode in die 4ppm- Kalibrierlösung ein. | Benutze dafür den grauen Deckel. | eintauchen.gif
808 | Fertig |  |  |  |  |  |  |  | 10 | Kalibrierung abgeschlossen | Den Auffangbehälter kannst du im normalen Abfluss entleeren. | leeren.gif
900 | DEMO
901 | Benötigte Teile |  |  |  |  |  |  |  | 45 | Stelle sicher, dass du folgende Teile bereit hast: | Ein 3V-Netzteil, einen PC Lüfter, Neodym-Magnete, einen Rührfisch, einen Schalter und eine Niedervoltbuchse. | raw/rührer_teile.gif
902 | Neodymmagnete aufkleben |  |  |  |  |  |  |  | 20 | Klebe die Neodymmagnete auf das Innere des Lüfters | Überprüfe mit einer anschließenden Testfahrt, ob diese fest genug sitzen. | raw/rührer_aufbau1.gif
903 | 3D-Druck Ding aufschrauben |  |  |  |  |  |  |  | 10 | Schraube das 3D-Druck Teil auf den Lüfter auf | Die Modellzeichnung findest du auf der Citizensensor Projektseite | raw/rührer_aufbau2.gif
904 | Magnetrührer fertif |  |  |  |  |  |  |  | 5 | Stelle nun einen Becher mit Wasser auf den Rührer | Gib den Rührfisch in den Becher dazu und teste, ob alles funktioniert. | raw/rührer_fertig.gif
910 | Methode 1: Fingerprobe |  |  |  |  |  |  |  | 5 | Mit dieser Methode kannst du schnell überprüfen, ob der Boden zu feucht oder zu trocken für eine valide Messung ist. | Tipp: Lockere den Boden zuerst mit einer Schaufel auf. | raw/fingerprobe.gif
911 | Methode 2: Handprobe |  |  |  |  |  |  |  | 10 | Diese genauere Methode hilft dir, abzuschätzen, wie du die Wasserzugabe vor der Messung korrigieren kannst. | Nimm dazu ein Stück Erde in die Hand und Drücke es zusammen. | raw/trocken_drücken.gif
912 | Methode 2: Feuchter Boden |  |  |  |  |  |  |  | 10 | Ist der Boden feucht, fühlt sich das anders an. Der Boden zerbröselt nicht so stark. | Zerreibe den Boden anschließend in der Hand und betrachte anschließend deine Handfläche | raw/feucht_drücken.gif
913 | Methode 2: Feuchter Boden |  |  |  |  |  |  |  | 5 | Ist der Boden feucht, ist deine Hand danach vermutlich noch schmutzig. | Versuche den Grad der Verschmutzung zu beurteilen. Das Bild zeigt starke Verschmutzung | raw/hand_dreckig.gif
914 | Methode 2: Trockener Boden |  |  |  |  |  |  |  | 10 | Ist der Boden trocken, ist deine Hand nach dem Zerbröseln sauber. | Auf der nächsten Seite siehst du die Bewertungsskala noch einmal als Übersicht. | raw/hand_sauber.gif
915 | Übersicht |  |  |  |  |  |  |  | 10 | Übersicht zur Beurteilung der Bodenfeuchte | 1: trockener Boden, 2: mitteltrockener Boden, 3: feuchter Boden, 4: nasser Boden | raw/übersicht.gif
920 | Bodenprobe verkleinern |  |  |  |  |  |  |  | 10 | Ca. 2 kg der genommenen Erdprobe abwiegen. | Darauf achten, dass keine groben Steine mehr enthalten sind. | raw/bodenprobe.gif
921 | Kegel auschütten |  |  |  |  |  |  |  | 20 | Schütte die Bodenprobe zu einem Kegel auf. | Achte auf einen ebenen Untergrund und einen möglichst gleichförmigen Kegel. | raw/kegel.gif
922 | Bodenprobe Vierteln |  |  |  |  |  |  |  | 10 | Teile den Erdkegel in vier gleich große Teile | Benutze eine dünne Platte aus Kunststoff oder Holz | raw/vierteln.gif
923 | Halbiere den Kegel |  |  |  |  |  |  |  | 10 | Probenmenge halbieren, indem diagonal gegenüberliegende Viertel des Erdkegels entfernt werden. | Die Probe wiegt nun nur noch 1 kg. | raw/halbiert.gif
924 | Schritte wiederholen |  |  |  |  |  |  |  | 10 | Wiederhole kegeln, vierteln und halbieren so oft, bis zu 500 g, 250g und schließlich 125g Bodenprobe hergestellt hast. | Fülle die Probenmenge anschließend in einen Plastikbecher. | raw/kleineprobe.gif
9999 | EXIT
1000 | ISA herstellen
1001 | Benötigte Utensilien |  |  |  |  |  |  |  | 10 | Überprüfe, ob alle benötigten Utensilien bereit stehen. | 500 ml Spritzflasche mit destilliertem Wasser, mind. 30 g Ammoniumsulfat ((NH4)2SO4, 1 verschließbarer Becher, 1 Rührfisch, 1 Messer, 100g Gewicht | kalibrierlösung_utensilien.gif
1002 | Salz abwiegen | calibration | y | Salz abwiegen | scale | calculated | y | scale | 40 | Wiege das Ammoniumsulfatsalz ab | Benutze einen kleinen Löffel und fang mit wenig an. Eine Messerspitz sind ca. 100 -500 mg. | salz_abwiegen.gif
1003 | Fülle Wasser ein | calibration | y | Wasser einfüllen | scale | calculated | y | scale | 30 | Fülle Wasser ein | Fülle möglichst exakt die angegebene Menge Wasser in den Becher ein. | gießen_demo.gif
1004 | Becher beschriften | calibration | y | Becher beschriften | scale | -30g +30g | y | scale | 50 | Beschrifte den Becher | Der angegebene Wert entspricht der Konzentration, die du tatsächlich hergestellt hast. Stelle den Becher anschließend wieder auf die Waage. | beschriften.gif
1005 | ISA hinzugeben |  |  |  |  |  |  |  | 10 | Pipettiere ISA in den Becher | Pipettiere die angebebene Menge Ionenstärkeanpasser (ISA = Ammoniumsulfatlösung) hinzu. | pipettieren.gif
1101 | Bodenprobe nehmen |  |  |  |  |  |  |  | 45 | Für die Entnahme von Bodenproben, beachte die Anleitung in unserem Wiki: | Nebenstehenden QR-Code mit dem Smartphone scannen. | probennahme.gif
1102 | Wässrige Lösung herstellen |  |  |  |  |  |  |  | 45 | Für die Herstellung einer wässrigen Lösung deiner Bodenprobe, beachte die Anleitung in unserem Wiki: | Nebenstehenden QR-Code mit dem Smartphone scannen. | loesung.gif
1103 | Kalibrieren und Messen |  |  |  |  |  |  |  | 45 | Hinweise zum Umgang mit der Nitratelektrode und zur Durchführung der Kalibrierung und Messung findest du in unserem Wiki: | Nebenstehenden QR-Code mit dem Smartphone scannen. | hinweise.gif

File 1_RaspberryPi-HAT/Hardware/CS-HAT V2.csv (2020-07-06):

Qty | Value | Package | Parts | Farnell | Mouser
1 | 1 | R1210 | R3
1 | 500 | R0805 | R18
1 | 910 | R0805 | R20
1 | 1,5k | R0805 | R22
1 | 1,8k | R0805 | R23
1 | 100k | R0805 | R10
2 | 10M | R0805 | R11, R12
8 | 10k | R0805 | R1, R2, R4, R5, R6, R7, R17, R19
2 | 1k | R0805 | R8, R27
1 | 33k | R0805 | R9
2 | 4,7k | R0805 | R25, R26
4 | 4,99k | R0805 | R13, R14, R15, R16
2 | 47k | R0805 | R21, R24
10 | 100n | C0805 | C6, C19, C20, C21, C22, C23, C24, C25, C27, C30
1 | 10n | C0805 | C7
4 | 47n | C0805 | C15, C16, C17, C18
3 | 10µ | C1206 | C12, C26, C28
2 | 15p | C0805 | C1, C2
1 | 1n | C0805 | C5
1 | 1µ | C1206 | C29
2 | 4,7µ | C1206 | C9, C13
4 | 470n | C0805 | C8, C10, C11, C14
1 | 16MHz | JXS53 | Q1 | 2854042 | 815-ABM3B-16-B2
1 | 32kHz | FC-12M | Q2 |  | 581-CX2016DB32000FPL
1 | 24LC32SN | SO-08 | IC8 | 9758003
1 | AD5293BRUZ-100 | TSSOP14 | IC6 | 2192233 | 584-AD5293BRUZ-100
1 | AD648JRZ | SO08 | IC4 | 1660964 | 584-AD648JRZ
1 | AD8226 | SO8 | IC3 | 1827360 | 584-AD8226ARZ
1 | ADUCM350BBCZ | BC_120_3 | IC1 | 2460461 | 584-ADUCM350BBCZ
1 | BME680 | BME680 | IC5 |  | 262-BME680
1 | MCP48X1SN | SO-08 | IC7 |  | 579-MCP4811-E/SN
1 | TS912B | SO08 | IC2 | 1750167 | 511-TS912BIDT
2 | FDN337 | SUPER-SOT3 | T1, T2 | 2323185 | 512-FDN337N
1 | PCIE03602-F-D-EMS2 | PCIE-036-02-F-D-EMS2 | X1 | 2085389
2 |  | 1X06S | JP4, JP5
1 |  | 1X08S | JP1
1 | RASPBERRY_PI_B+_DIM | RASPBERRY_PI_BPLUS_DIM | PCB1 | 1569230 | 855-M20-6102045
2 | RESET, Serial Boot | SKHMPXE010 | S2 | 2056838 | SKHMQMG020
8 | TESTPLUG2MM | TESTPLUG2MM | TP1, TP2, TP3, TP4, TP5, TP6, TP7, TP8 | 2292857 schwarz 1307228 rot 1307241 blau 1307216 grün 1307186 weiß 1654712 gelb

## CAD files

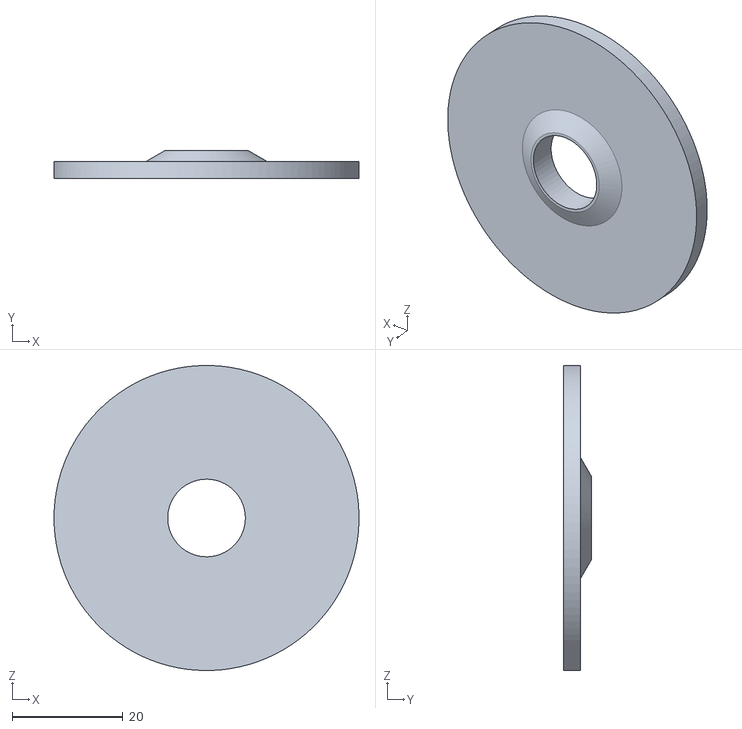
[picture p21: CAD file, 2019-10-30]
5_Enclosure/CS_v2.0_Waage_Abschluss.stl
55.0 x 5.00 x 55.0

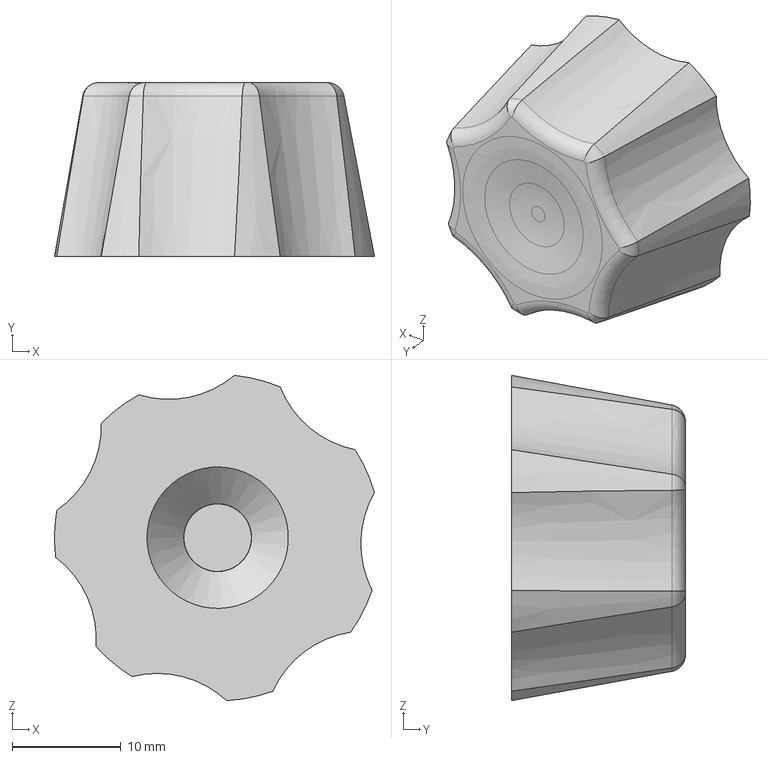
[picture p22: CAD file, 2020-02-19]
5_Enclosure/step/knob.step
29.4 x 16.0 x 29.9 mm

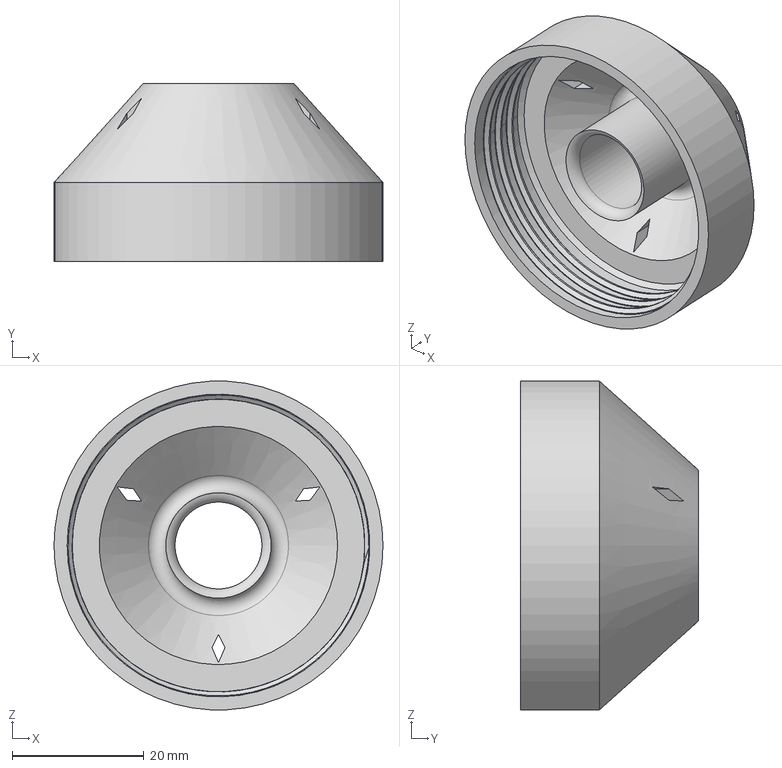
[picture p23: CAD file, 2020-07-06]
6_Accessories/cup_cap/cup_cap.step
50.0 x 27.0 x 49.9 mm

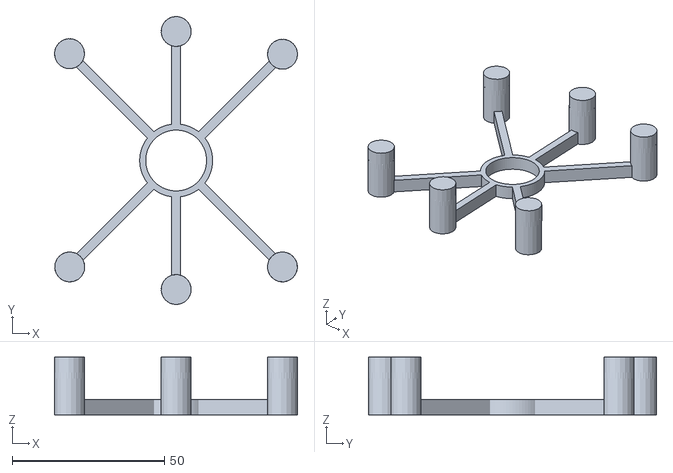
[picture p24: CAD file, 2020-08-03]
6_Accessories/orbital_shaker/CitizenSensor_OrbitalShaker_Top.stl
79.9 x 94.7 x 19.0

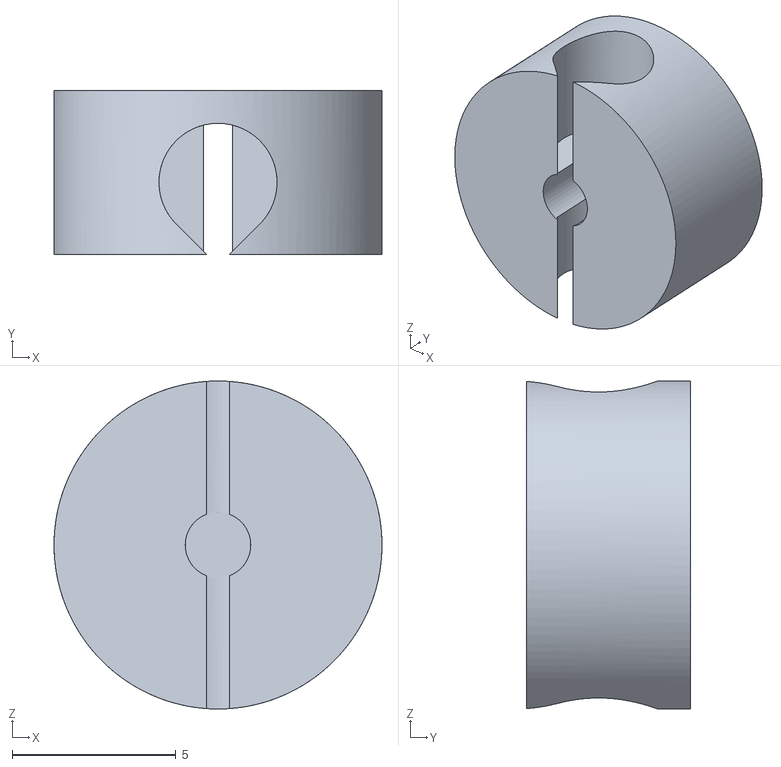
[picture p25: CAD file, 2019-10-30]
5_Enclosure/CS_v2.0_Mixer_Rotor.stl
10.0 x 5.00 x 10.0

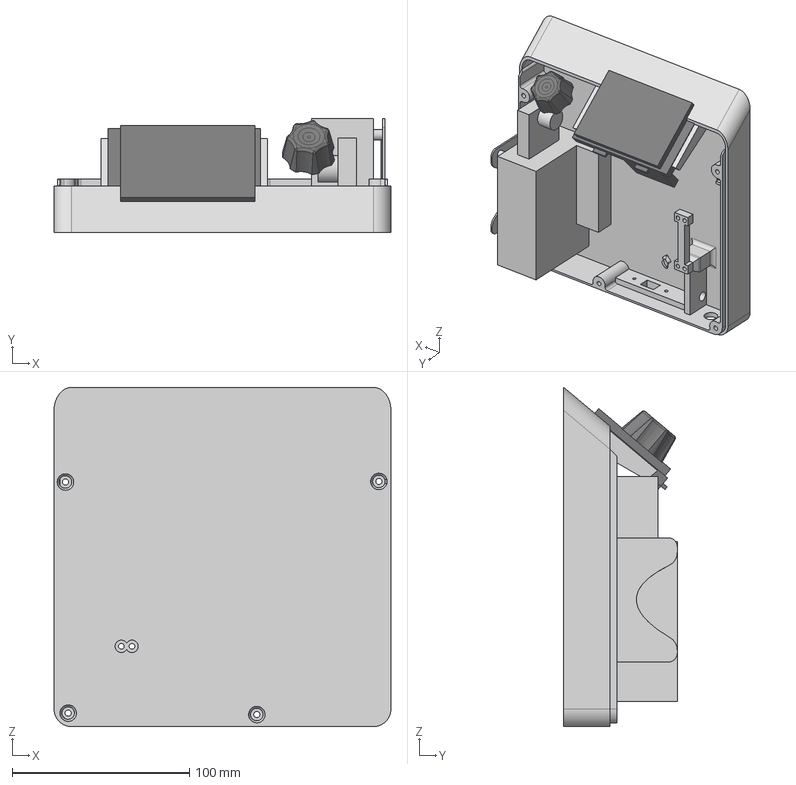
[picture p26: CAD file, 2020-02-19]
5_Enclosure/step/enclosure.step
190.0 x 64.0 x 191.3 mm
knob
Display
Electronics
Load Cell

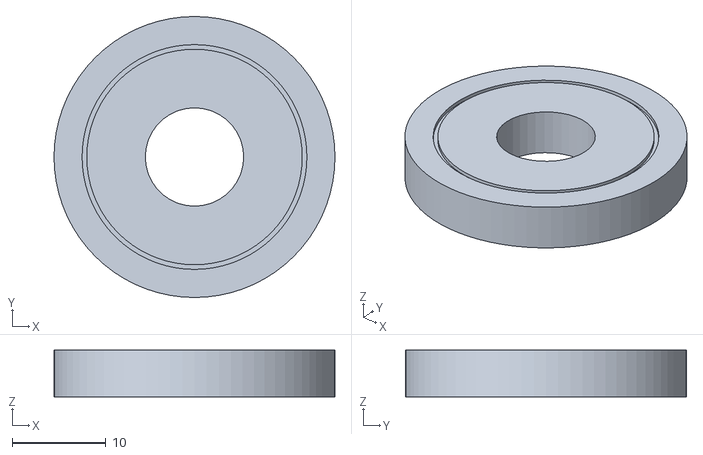
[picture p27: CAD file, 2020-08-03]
6_Accessories/orbital_shaker/CitizenSensor_OrbitalShaker_Disc.stl
30.0 x 30.0 x 5.00

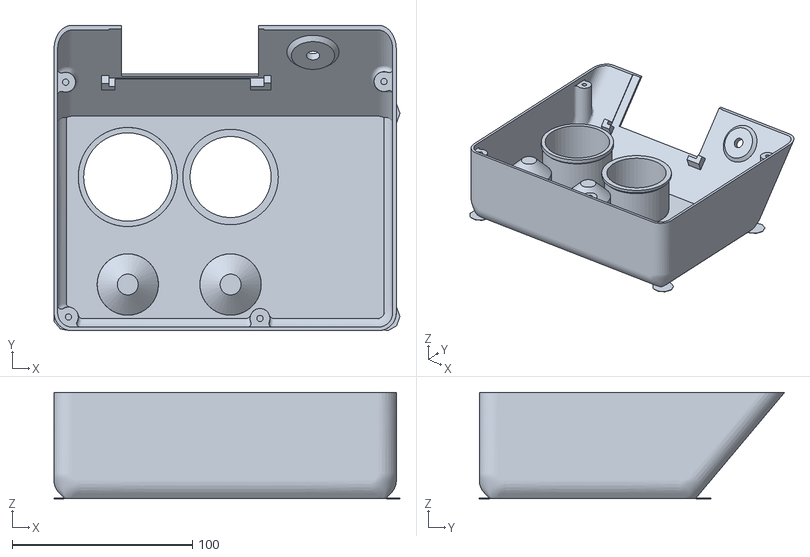
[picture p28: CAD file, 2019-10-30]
5_Enclosure/CS_v2.0_Top_WithPadsForPrintingWithoutBrim.stl
192.0 x 169.5 x 59.0

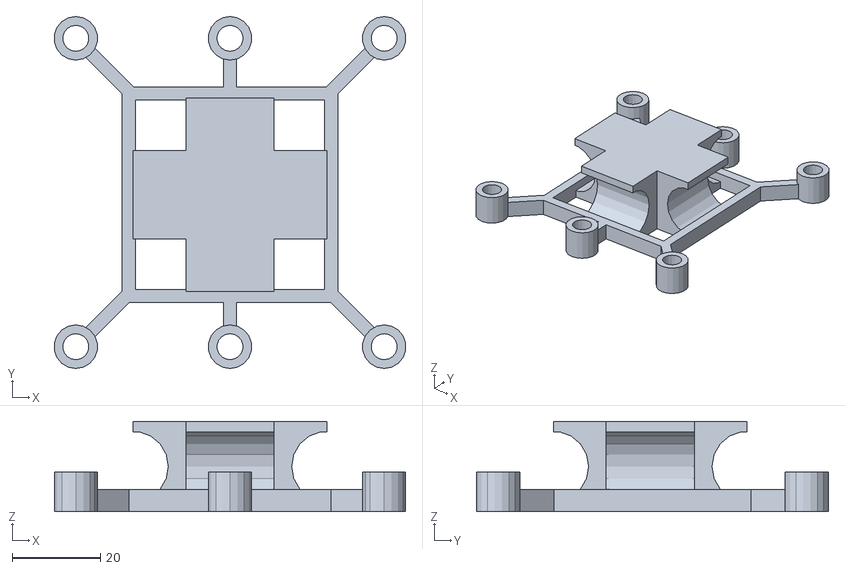
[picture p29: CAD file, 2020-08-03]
6_Accessories/orbital_shaker/CitizenSensor_OrbitalShaker_Base.stl
79.7 x 79.9 x 20.5

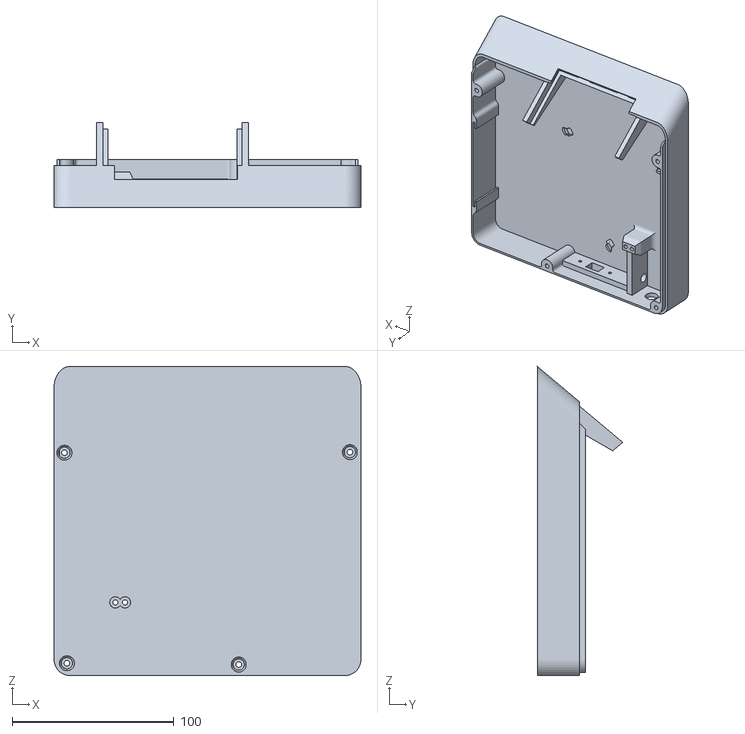
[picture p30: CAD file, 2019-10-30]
5_Enclosure/CS_v2.0_Base.stl
190.0 x 52.9 x 191.3

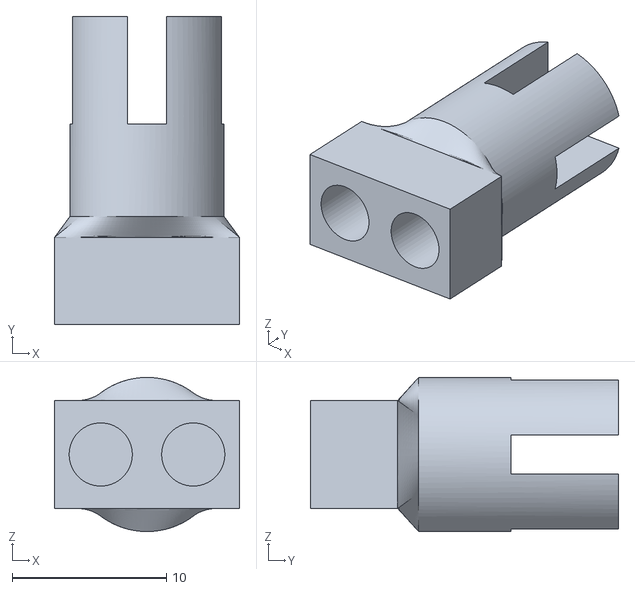
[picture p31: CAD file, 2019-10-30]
5_Enclosure/CS_v2.0_Waage_Fuss.stl
12.0 x 20.0 x 10.0

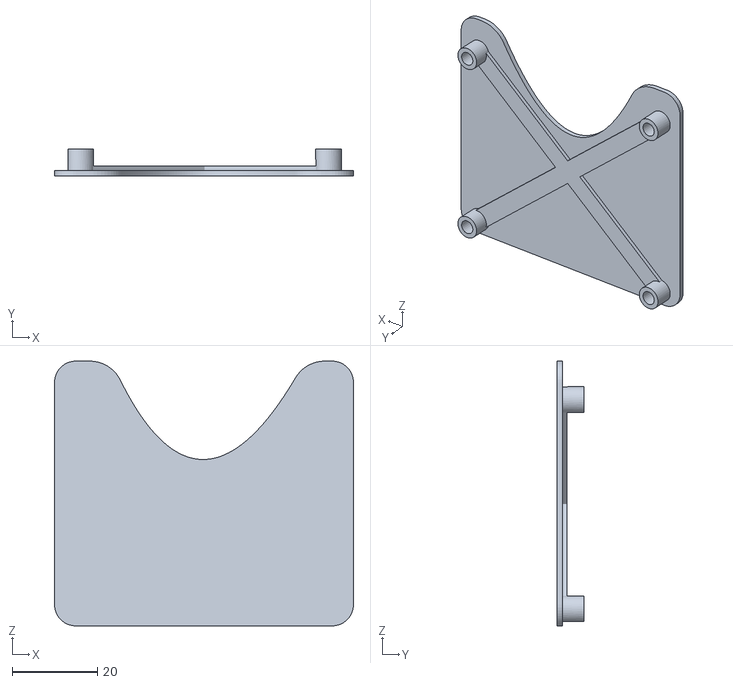
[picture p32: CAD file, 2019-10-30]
5_Enclosure/CS_v2.0_RaspiHolder.stl
70.0 x 6.25 x 62.0

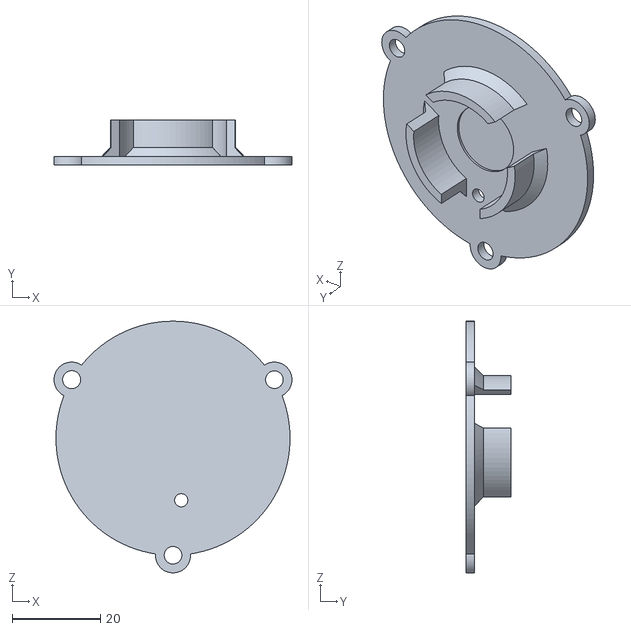
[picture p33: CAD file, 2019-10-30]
5_Enclosure/CS_v2.0_Mixer_MotorHalter.stl
54.0 x 10.3 x 57.1

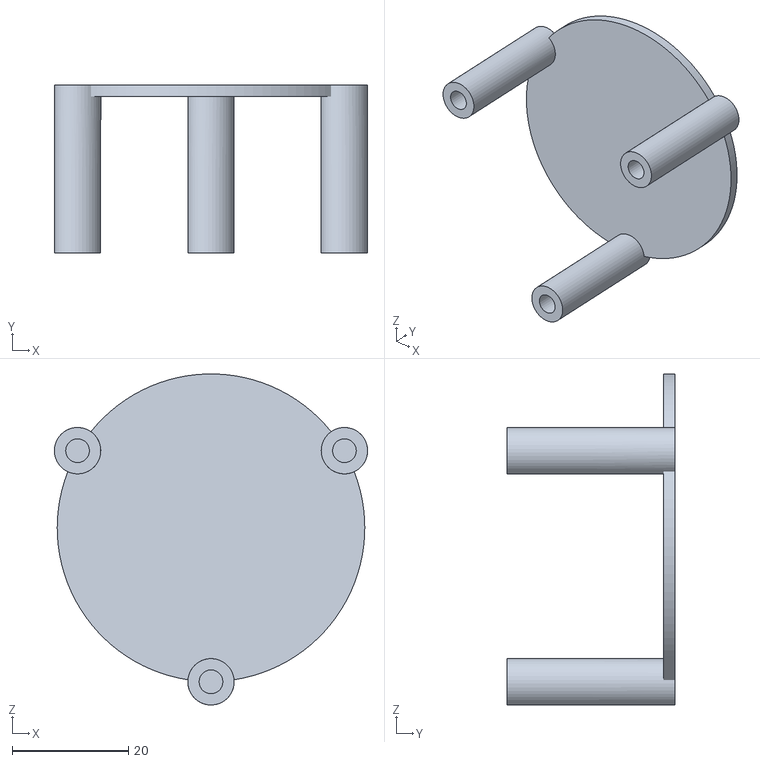
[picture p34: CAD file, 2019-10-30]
5_Enclosure/CS_v2.0_Mixer_Boden.stl
54.0 x 29.0 x 57.0

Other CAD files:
5_Enclosure/step/cap.step
5_Enclosure/CS_v2.0_Knob.stl
5_Enclosure/CS_v2.0_Top.stl
5_Enclosure/CS_v2.0_Waage_Boden.stl
5_Enclosure/fusion360/cap v7.f3d
5_Enclosure/fusion360/enclosure v64.f3z
5_Enclosure/fusion360/knob v5.f3d
6_Accessories/cup_cap/cup_cap.stl

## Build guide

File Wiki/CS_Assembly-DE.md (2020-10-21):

[English version of this page](https://github.com/CitizenSensor/CitizenSensor/blob/master/Wiki/CS_Assembly.md)

# CitizenSensor Montage #

Folgende Schritte sind nötig, um das CitizenSensor Gerät zu montieren:

1. RaspberryPi-HAT Montage
2. Elektrometer Montage
3. Connector Board Montage
4. Enclosure 3D Druck
5. CitizenSensor Endmontage

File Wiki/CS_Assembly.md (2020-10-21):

[Deutsche Version dieser Seite](https://github.com/CitizenSensor/CitizenSensor/blob/master/Wiki/CS_Assembly-DE.md)

# CitizenSensor Assembly #

Proceed in this order to assemble the CitizenSensor device:

1. RaspberryPi-HAT Assembly
2. Elektrometer Assembly
3. Connector Board Assembly
4. Enclosure 3D Printing
5. CitizenSensor Device Final Assembly

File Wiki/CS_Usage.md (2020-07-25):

[Deutsche Version dieser Seite](https://github.com/CitizenSensor/CitizenSensor/blob/master/Wiki/CS_Usage-DE.md)

# CitizenSensor Usage #

The CitizenSensor device enables the measurement of nitrate in soil. The measuring device works with an electrochemical sensor that can determine the nitrate content in aqueous solutions.

For a nitrate measurement in soil, therefore, several steps must first be taken to produce an aqueous solution from a soil sample.

The accuracy of the nitrate measurement result depends strongly on how carefully the soil sample is taken and prepared.

We therefore recommend following the steps in the following instructions as closely as possible.

1. [Soil Sampling](https://github.com/CitizenSensor/CitizenSensor/blob/master/Wiki/CS_Usage_SoilSampling.md)
2. [Soil Preparation](https://github.com/CitizenSensor/CitizenSensor/blob/master/Wiki/CS_Usage_SoilPreparation.md)
3. [Creation of Aqueous Solution](https://github.com/CitizenSensor/CitizenSensor/blob/master/Wiki/CS_Usage_AqueousSolution.md)
4. [Preparation of Nitrate Measurement](https://github.com/CitizenSensor/CitizenSensor/blob/master/Wiki/CS_Usage_Preparation.md)
5 [Nitrate Measurement](https://github.com/CitizenSensor/CitizenSensor/blob/master/Wiki/CS_Usage_Measurement.md)
6. [Interpretation of Measurements](https://github.com/CitizenSensor/CitizenSensor/blob/master/Wiki/CS_Usage_Interpretation.md)

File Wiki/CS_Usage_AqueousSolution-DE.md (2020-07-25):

[English version of this page](https://github.com/CitizenSensor/CitizenSensor/blob/master/Wiki/CS_Usage_AqueousSolution.md)

# Herstellung der Wässrigen Lösung #

## Grundlagenwissen zur Herstellung einer Wässrigen Lösung ##

Für die Nitratmessung wird eine wässrige Lösung der Bodenprobe benötigt. Diese wässrige Lösung wird in zwei Schritten hergestellt: 

1. Lösen der Bodenprobe durch Schütteln
2. Filtrieren der gelösten Bodenprobe

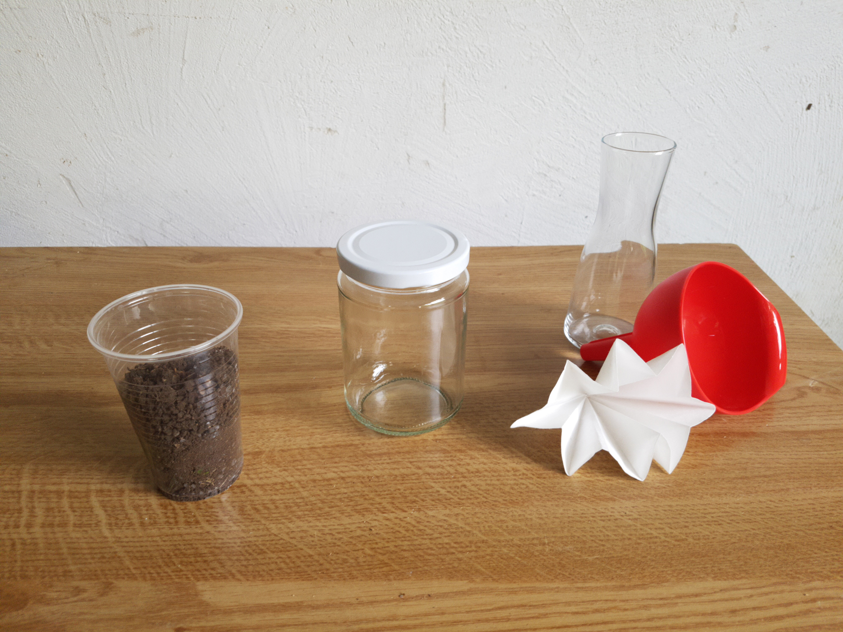
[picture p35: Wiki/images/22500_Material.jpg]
Material für Herstellung Wässrige Lösung

_Bild 1: Material für die Herstellung einer Wässrigen Lösung_

Bei der Planung der Nitratmessung sollte berücksichtigt werden, dass die Herstellung der wässrigen Lösung ein relativ langwieriger Prozess ist: sowohl das Schütteln, als auch die Filtration der wässrigen Lösung dauern zwei Stunden.

Die Filtration kann dadurch beschleunigt werden, dass eine Bodenprobe auf zwei Filter verteilt wird. Die Filterzeit kann so durch das parallele Filtern mit mehreren Filtern eventuell etwas verkürzt werden.

### Lösen der Bodenprobe ### 
Das Lösen der Bodenprobe wird durch Auffüllen mit Destilliertem Wasser und längerem Schütteln erreicht. Dabei wird zunächst fünf Minuten mit der Hand geschüttelt um größere Erdklumpen zu zerkleinern. Anschließend wird über zwei Stunden maschinell geschüttelt um alle Bodenbestandteile aus der Bodenprobe zu lösen.
Für das maschinelle Schütteln können professionelle Schüttelgeräte, aber auch selbstgebaute Schüttler aus günstigen Bauteilen verwendet werden.

### Filtrieren der gelösten Bodenprobe ###
Für das Filtrieren der gelösten Bodenprobe wird ein Feinfilter mit 10 µm Porengröße eingesetzt. Es sollte darauf geachtet werden, dass es ein "nitratarmer" Filter verwendet wird, da andernfalls das Messergebnis durch Nitrat im Filtermaterial verfälscht werden könnte.

Für das Filtrieren ist außer dem Filter, einem Trichter und einem Glasgefäß kein weiteres Zubehör erforderlich.

Beim Filtern entsteht nach etwa zwei Stunden als Endergebnis eine klare Flüssigkeit, in der alle Bodenbestandteile gelöst sind. 

## Werkzeug und Materialien für die Herstellung einer Wässrigen Lösung ##

- **Plastikbecher mit Bodenprobe** (Ergebnis aus Schritt "Probenaufbereitung")
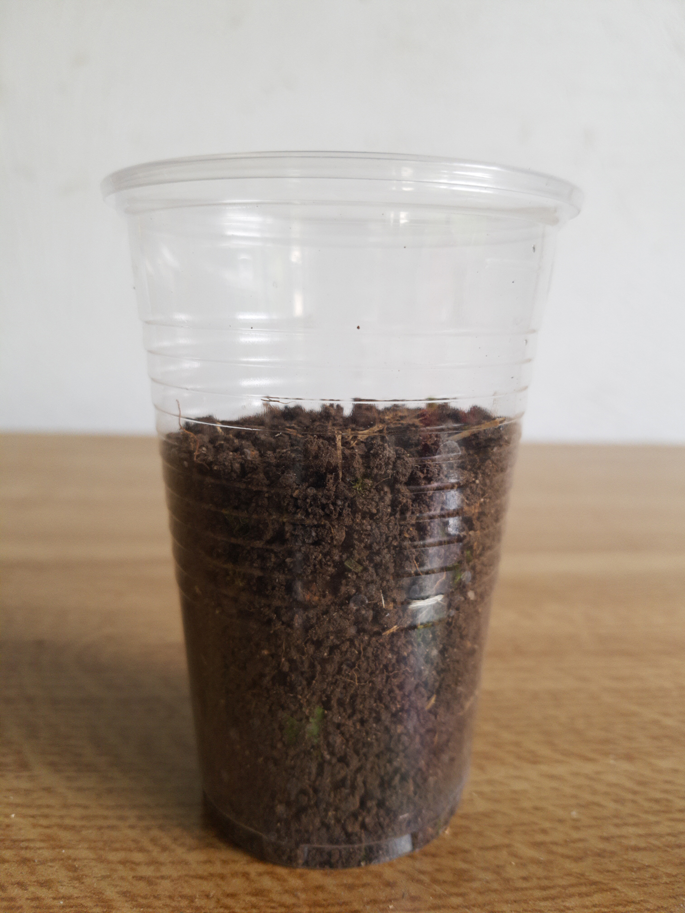
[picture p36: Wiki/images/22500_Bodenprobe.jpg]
Plastikbecher mit Bodenprobe

_Bild 2: Bodenprobe_
- **Marmeladenglas mit Deckel**
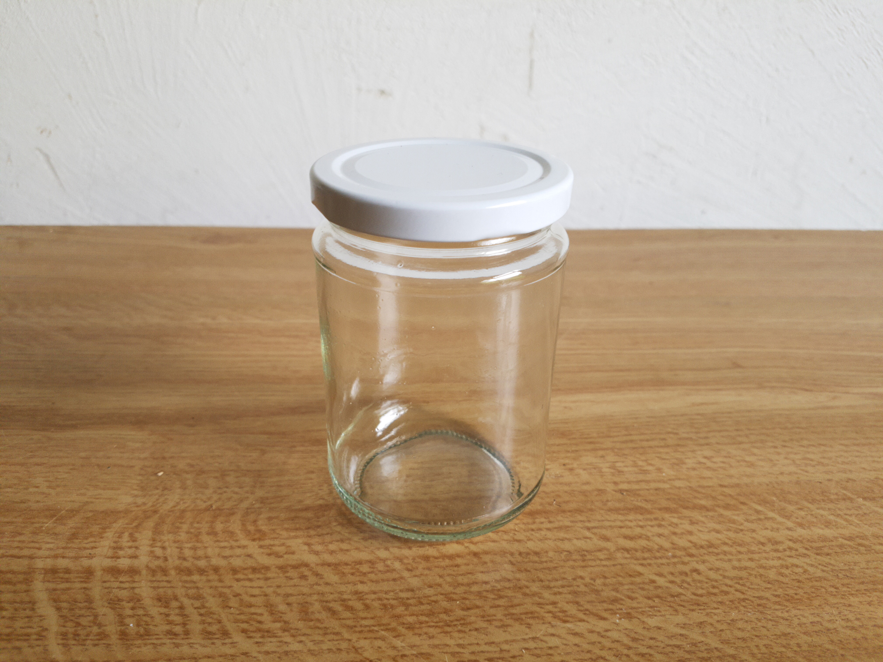
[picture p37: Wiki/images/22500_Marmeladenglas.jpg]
Marmeladenglas

_Bild 3: Marmeladenglas_
- **Filterpapier**
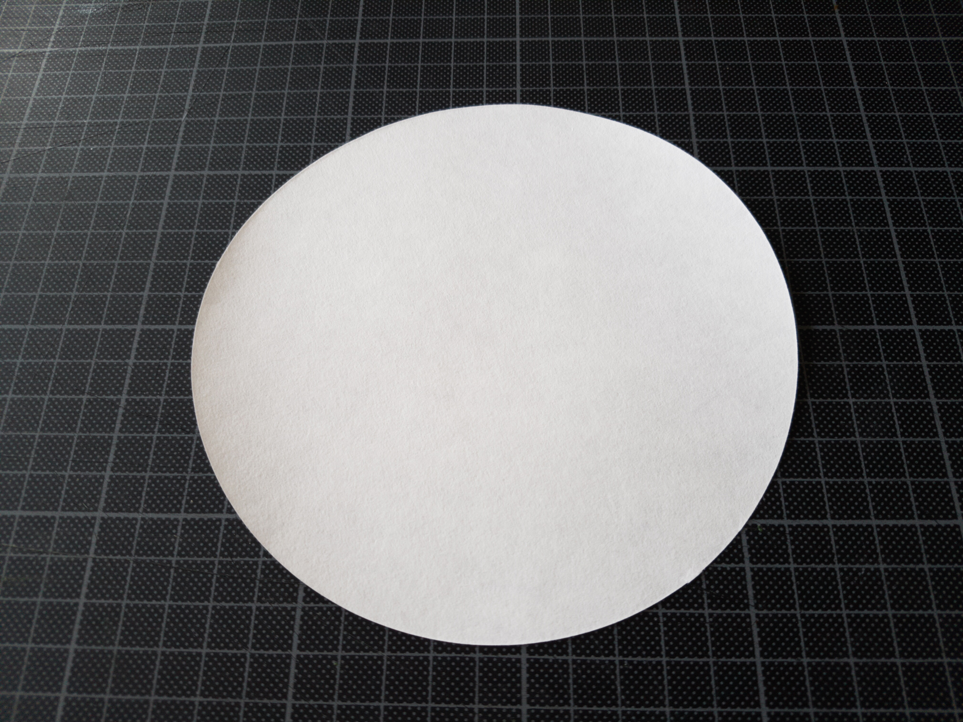
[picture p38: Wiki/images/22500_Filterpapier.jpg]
Filterpapier

_Bild 4: Filterpapier_
- **Blumenvase** (z.B. IKEA [TIDVATTEN](https://www.ikea.com/de/de/cat/tidvatten-serie-38431))
- **Trichter** (z.B. IKEA [CHOSIGT](https://www.ikea.com/de/de/p/chosigt-trichter-2er-set-versch-farben-70153179/))
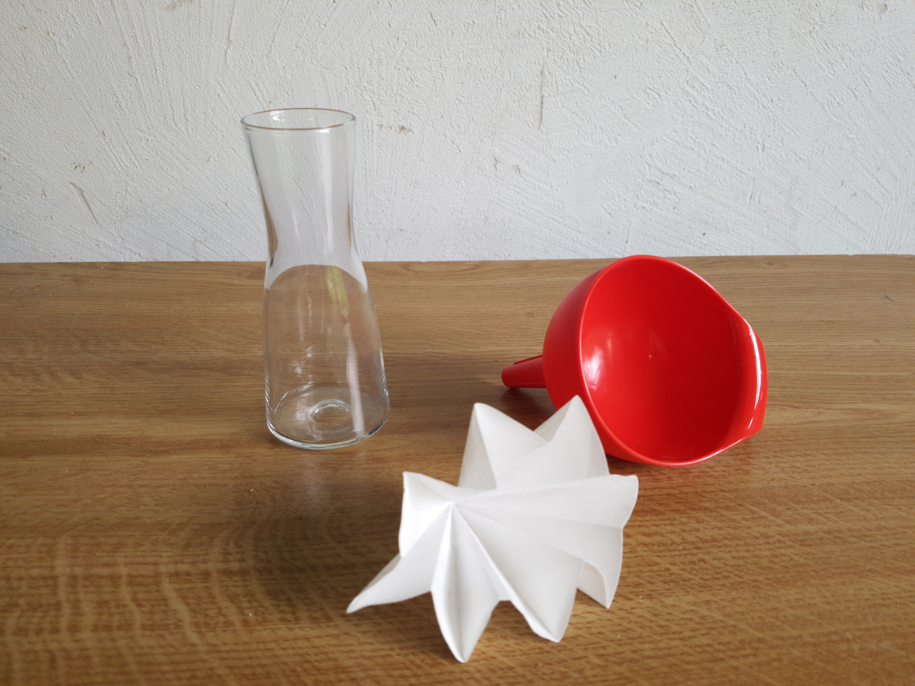
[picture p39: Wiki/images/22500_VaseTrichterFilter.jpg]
Blumenvase mit Trichter und Filterpapier

_Bild 5: Blumenvase mit Trichter und Filterpapier_
- **Destilliertes Wasser**
- **Schüttelgerät**
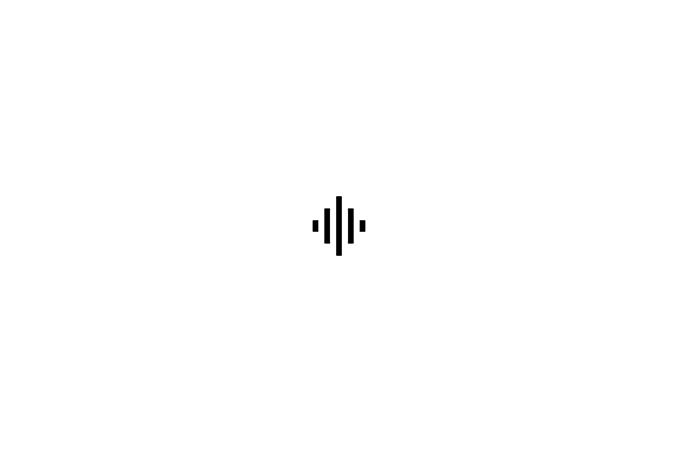
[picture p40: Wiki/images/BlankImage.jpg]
Schüttelgerät

_Bild 6: Schüttelgerät_

## Vorgehensweise zur Herstellung einer Wässrigen Lösung ##

### Bodenprobe Lösen und Schütteln ###

1. **Bodenprobe in Marmeladenglas füllen**
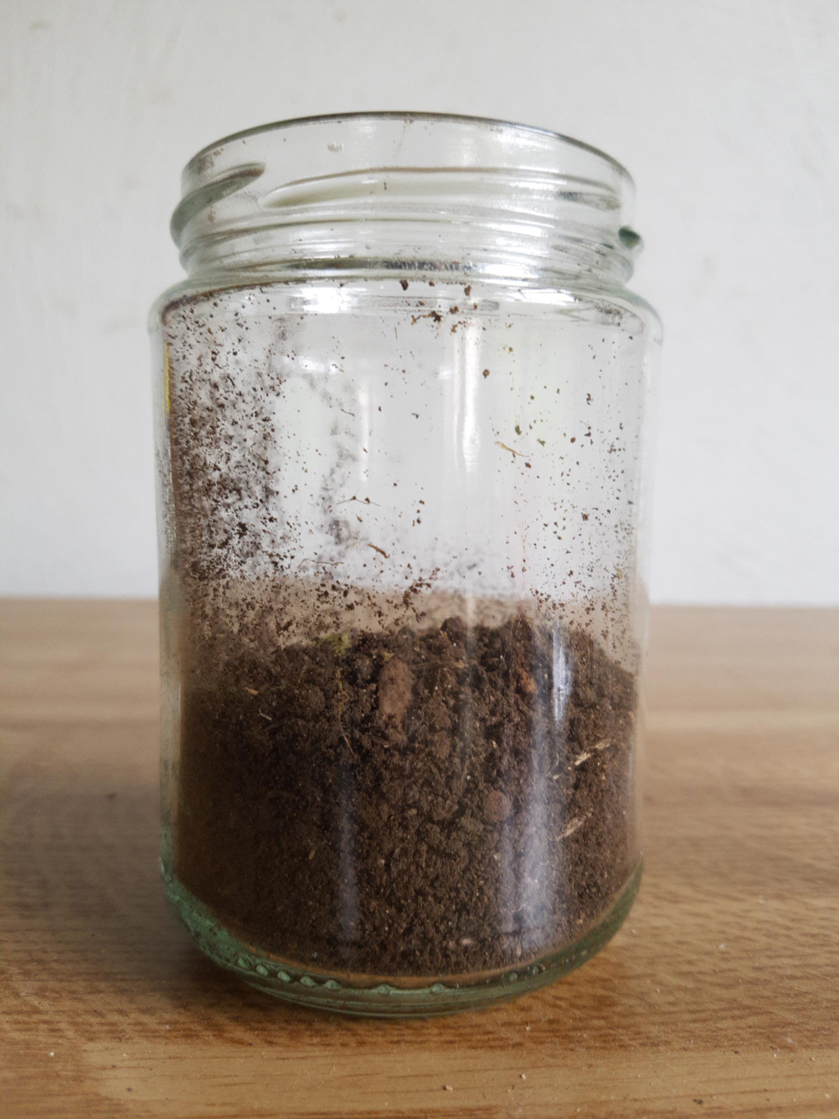
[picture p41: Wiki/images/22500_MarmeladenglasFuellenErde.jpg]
Marmeladenglas füllen

_Bild 7: Marmeladenglas füllen_

2. **Bodenprobe mit Destilliertem Wasser auffüllen**
Es sollte so lange Destilliertes Wasser aufgefüllt werden, bis die Bodenprobe komplett unter Wasser steht. 
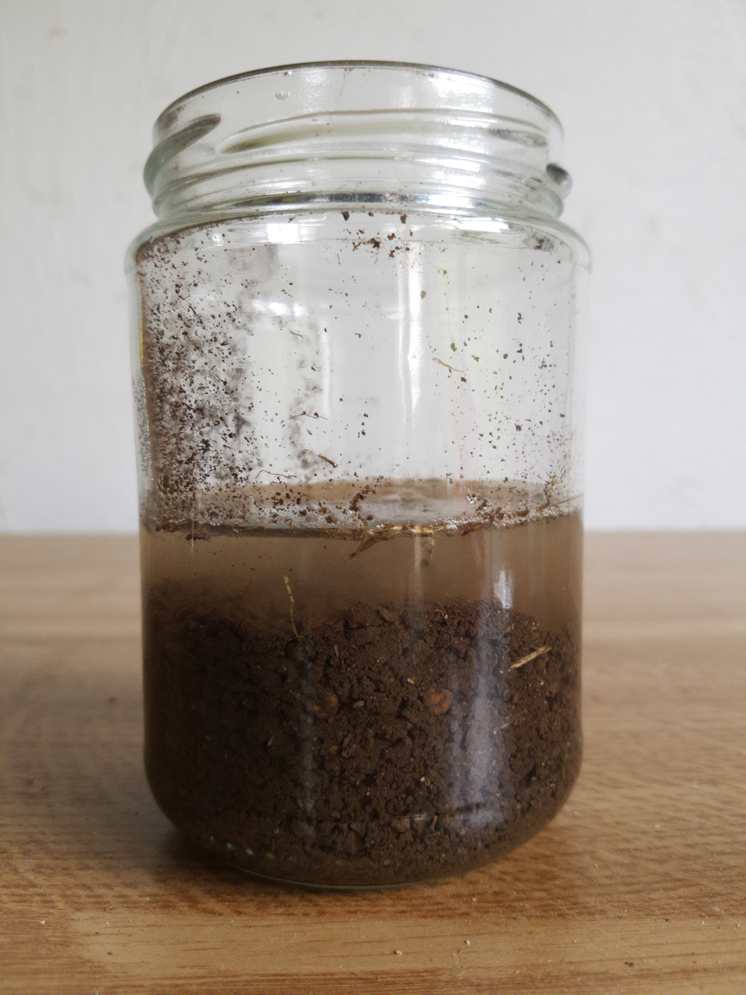
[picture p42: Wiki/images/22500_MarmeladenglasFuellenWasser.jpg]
Marmeladenglas mit Wasser füllen

_Bild 8: Marmeladenglas mit Wasser füllen_

3. **Bodenprobe fünf Minuten schütteln**
Durch das Schütteln der Bodenprobe entsteht eine schlammige Lösung aus Erde und Wasser.
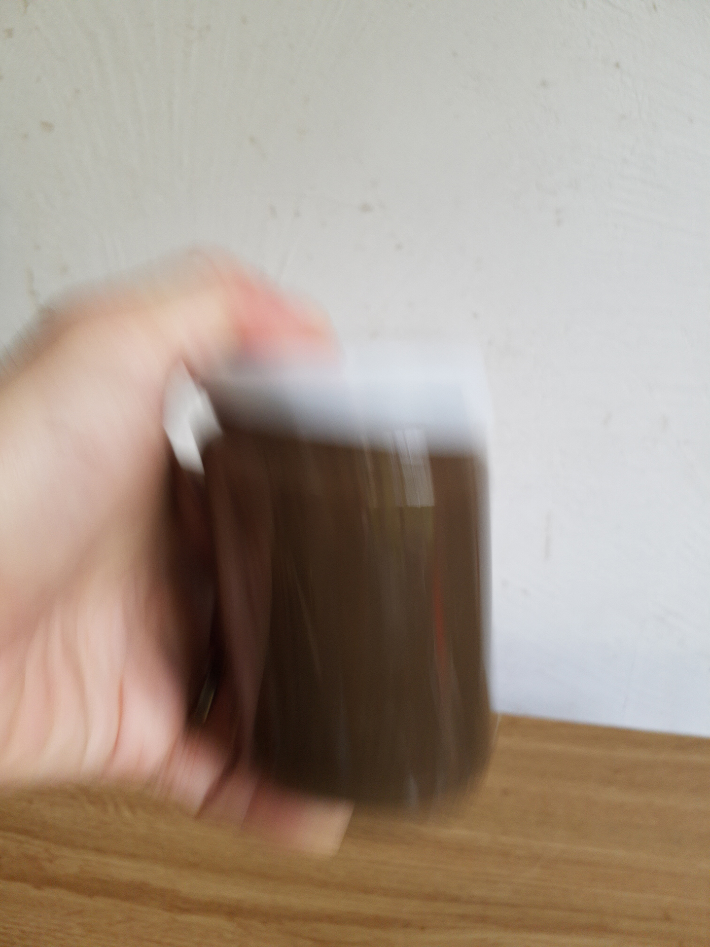
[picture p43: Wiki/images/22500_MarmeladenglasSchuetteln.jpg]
Marmeladenglas schütteln

_Bild 9: Marmeladenglas schütteln_

3. **Bodenprobe gründlich schütteln**
Die Bodenprobe muss über zwei Stunden gründlich geschüttelt werden um alle Bodenbestanteile zu lösen.
Schütteln mit CitizenSensor Shaker
_Bild 10: Schütteln mit CitizenSensor Shaker_
Schütteln mit CitizenSensor Orbital Shaker
_Bild 11: Schütteln mit CitizenSensor Orbital Shaker_

Durch das Schütteln ergibt sich eine schlammige Lösung der Bodenprobe
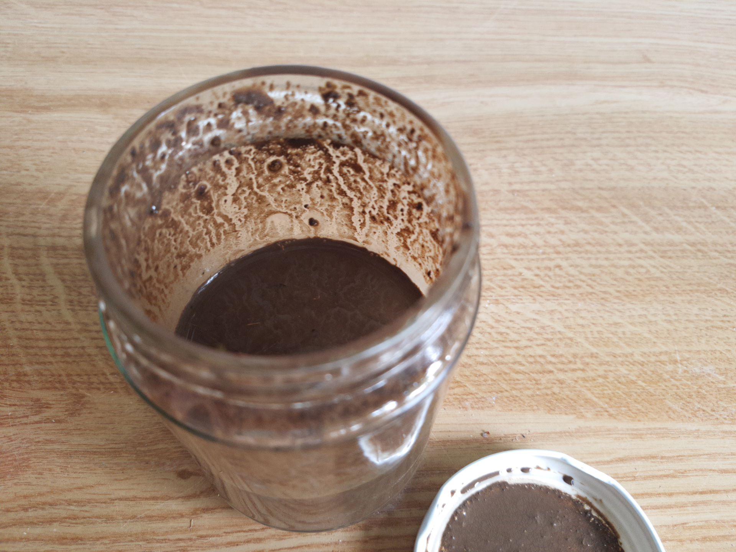
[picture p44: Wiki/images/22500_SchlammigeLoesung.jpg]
Schlammige Lösung

_Bild 12: Schlammige Lösung der Bodenprobe_

### Bodenprobe Filtrieren ###

Für das Filtrieren der Bodenprobe muss zunächst das Filterpapier gefaltet werden.

1. **Filterpapier falten**
Die runde Filterpapierscheibe wird viermal mittig gefaltet. Es entsteht ein sechzehntel Kreisausschnitt. 
Filterpapier
_Bild 13: Filterpapier_
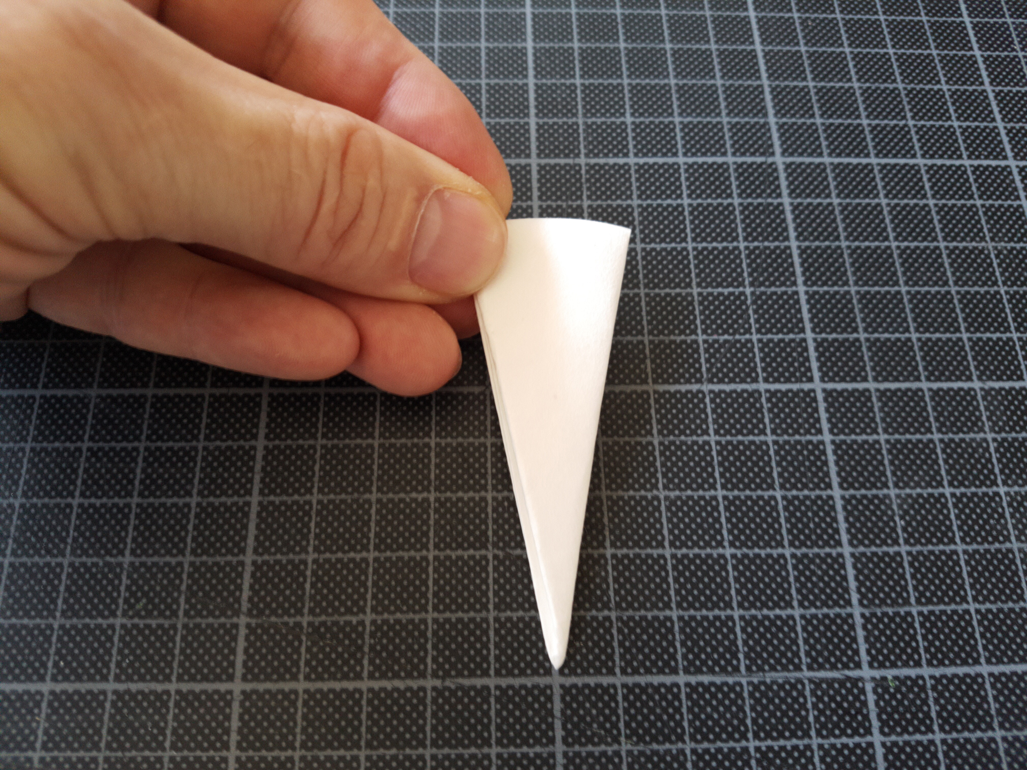
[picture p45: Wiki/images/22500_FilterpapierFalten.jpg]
Filterpapier Falten

_Bild 14: Filterpapier falten_

2. **Filterpapier auffalten**
Die Filterpapierscheibe wird wieder aufgefaltet. Man sieht die Falze der sechzehn Kreissegmente. 
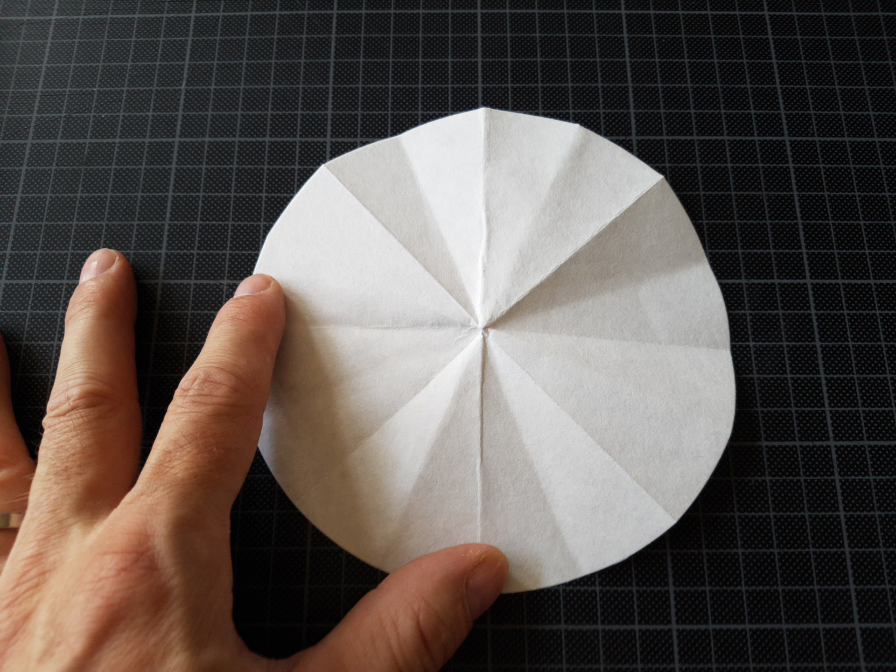
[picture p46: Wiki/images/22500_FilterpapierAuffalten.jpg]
Filterpapier Falten

_Bild 15: Filterpapier auffalten_

3. **Filterpapier Zickzack falten**
Die Falze im Filterpapier werden abwechselnd nach unten und oben gefaltet. Es ensteht ein Kegelförmiger Filter mit Zickzack-Rand.
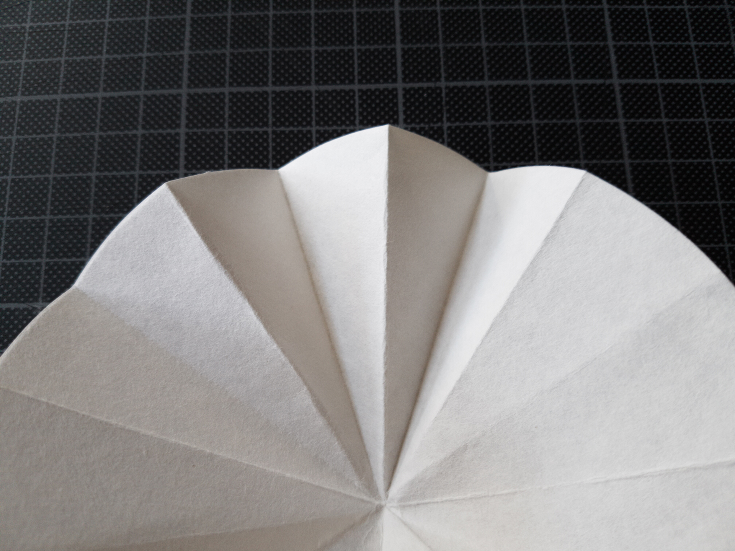
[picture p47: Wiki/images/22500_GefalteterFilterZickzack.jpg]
Filter falten

_Bild 16: Filter falten_
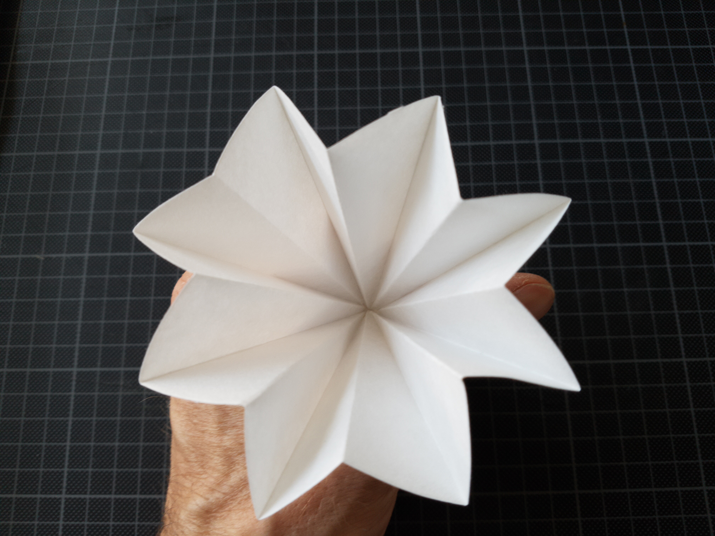
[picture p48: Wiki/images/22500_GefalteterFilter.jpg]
Gefalteter Filter

_Bild 17: Gefalteter Filter_

Mit dem fertig gefalteten Filter kann nun die wässrige Lösung der Bodenproge hergestellt werden.

1. **Trichter in Vase stellen** und gefaltetes Filterpapier einlegen
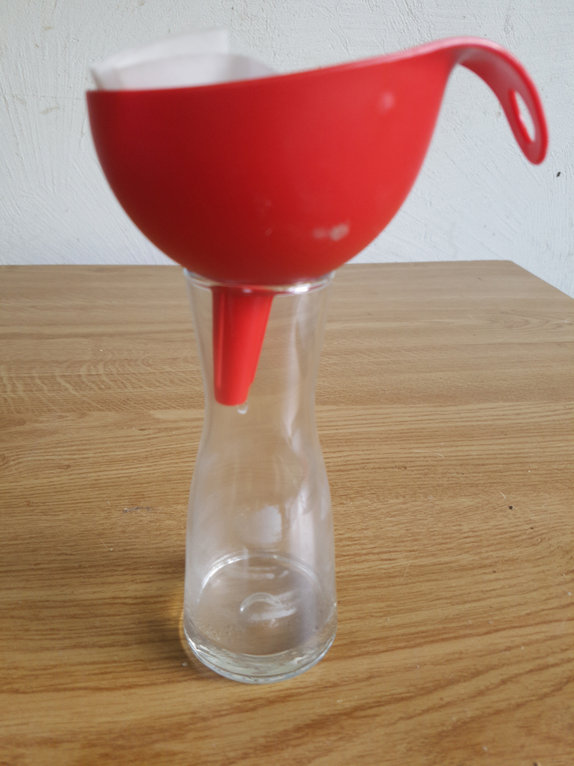
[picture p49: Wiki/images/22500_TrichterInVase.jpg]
Trichter in Vase stellen

_Bild 18: Trichter in Vase stellen_

2. **Geschüttelte Bodenprobe in Filter füllen**
Der Erdschlamm sollte nur bis knapp unter den Rand eingefüllt werden, 
damit der Filter stabil bleibt und kein Erdschlamm überläuft.
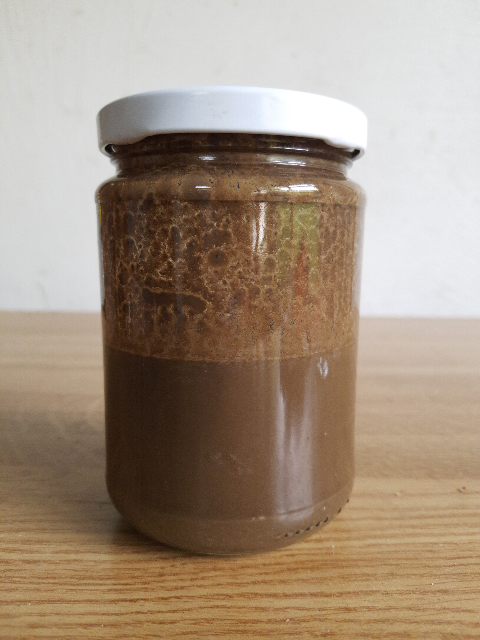
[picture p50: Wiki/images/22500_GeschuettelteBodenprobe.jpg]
Geschüttelte Bodenprobe

_Bild 19: Geschüttelte Bodenprobe_
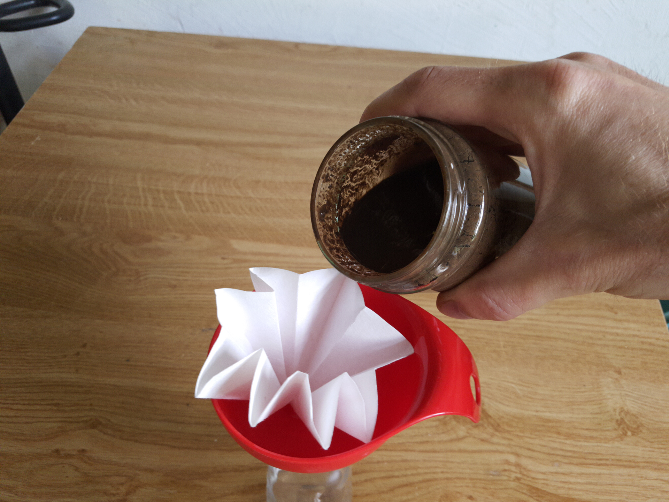
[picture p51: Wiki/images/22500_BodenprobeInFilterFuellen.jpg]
Bodenprobe in Filter füllen

_Bild 20: Bodenprobe in Filter füllen_
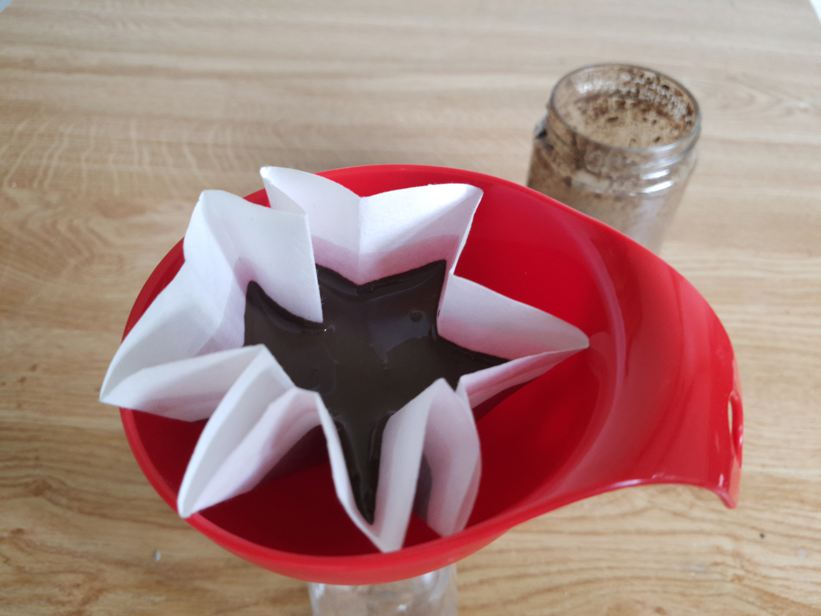
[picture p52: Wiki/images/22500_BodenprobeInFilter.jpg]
Bodenprobe in Filter

_Bild 21: Bodenprobe in Filter_
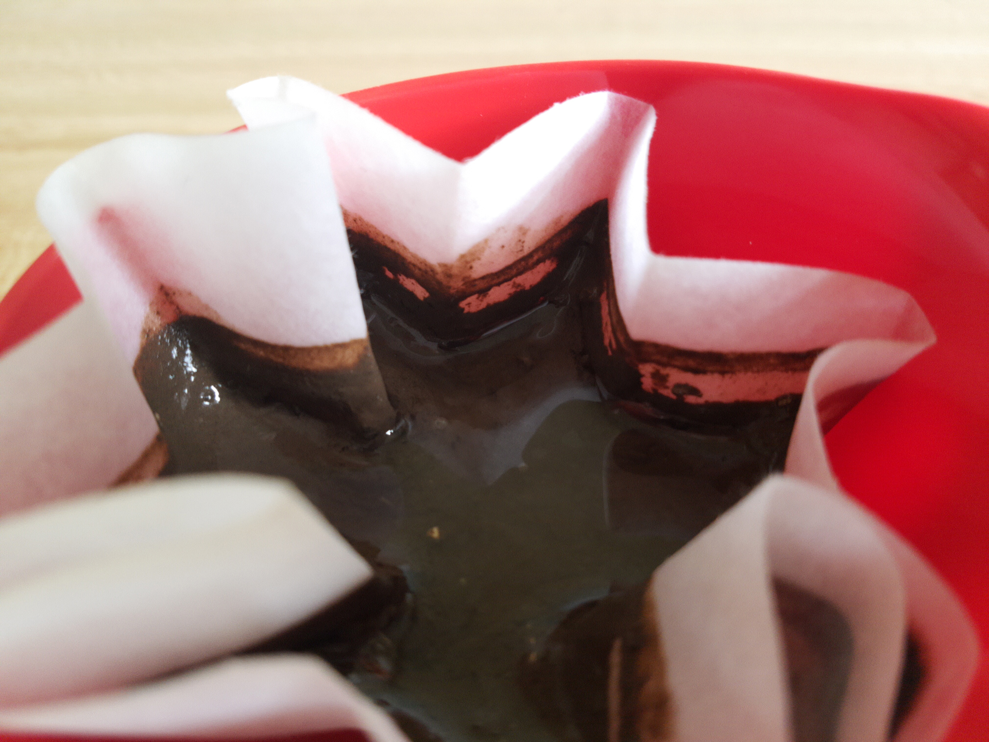
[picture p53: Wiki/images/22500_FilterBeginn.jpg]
Bodenprobe in Filter zu Beginn

_Bild 22: Bodenprobe in Filter zu Beginn_

3. **Bodenprobe zwei Stunden filtrieren**
Das Filtrieren der Bodenprobe dauert ungefähr zwei Stunden. 
Anfangs tropft die wässrige Lösung der Bodenprobe noch relativ schnell aus dem Trichter in die Vase (etwa alle 5 Sekunden ein Tropfen).
Später verlangsamt sich die Frequenz der Tropfen auf etwa einen Tropfen alle 20 Sekunden.
Die Filtration ist dann beendet, wenn auf dem Bodensatz im Filter keine Flüssigkeit mehr steht.
Das Filtrat in der Vase sollte eine klare Flüssigkeit sein.
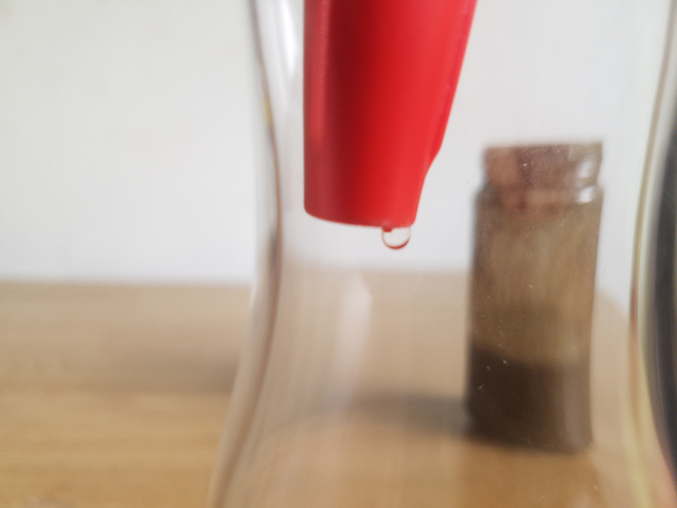
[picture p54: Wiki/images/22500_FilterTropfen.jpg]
Wässrige Lösung Tropfen

_Bild 23: Wässrige Lösung tropft aus dem Filter_
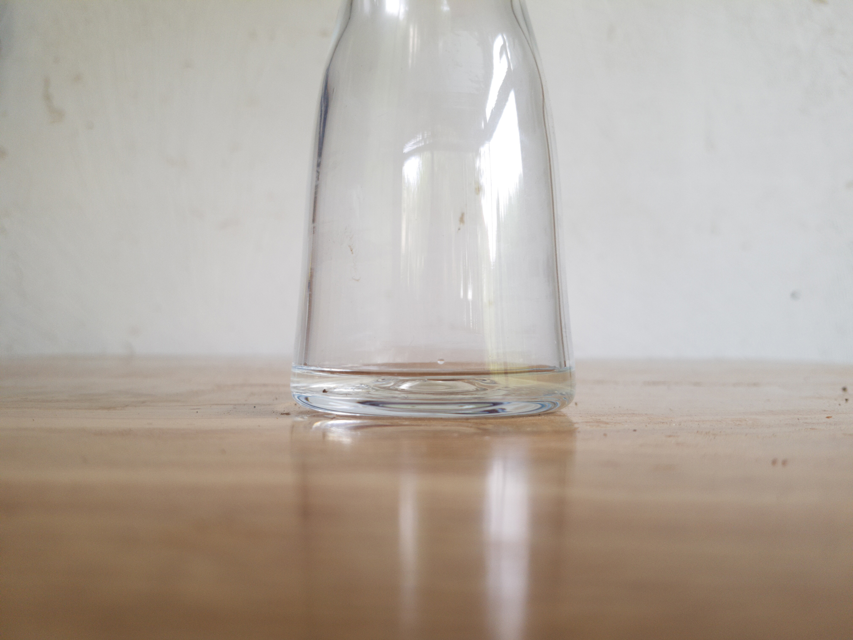
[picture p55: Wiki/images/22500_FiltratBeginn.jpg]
Wässrige Lösung zu Beginn

_Bild 24: Wässrige Lösung zu Beginn_
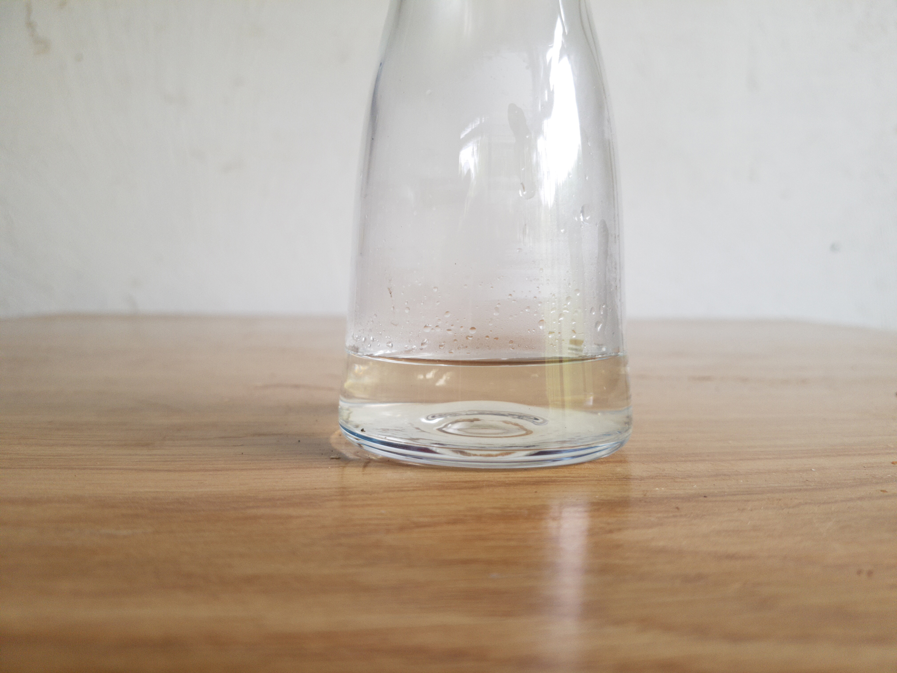
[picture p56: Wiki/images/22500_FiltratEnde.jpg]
Wässrige Lösung am Ende

_Bild 25: Wässrige Lösung am Ende_
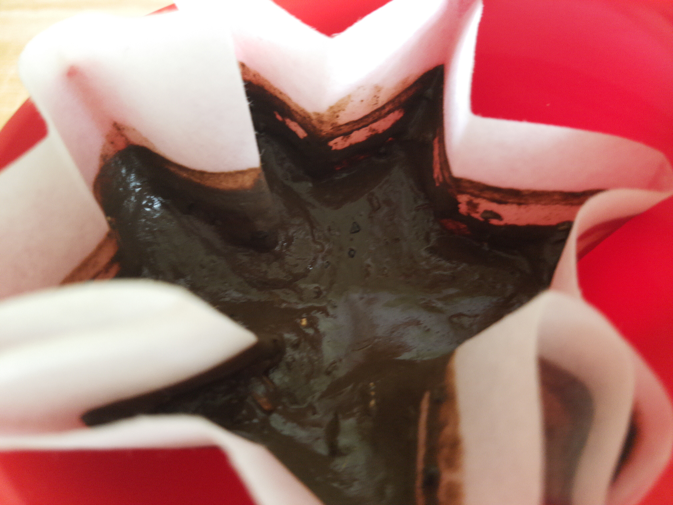
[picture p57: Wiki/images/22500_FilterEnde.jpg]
Bodenprobe in Filter am Ende

_Bild 26: Bodenprobe in Filter am Ende_

4. **Wässrige Lösung Umfüllen**
Das Filtrat wird aus der Vase in einen Plastikbecher umgefüllt und beschriftet.
Damit ist die wässrige Lösung der Bodenprobe für die Nitratmessung fertig!
Wässrige Lösung umfüllen
_Bild 27: Wässrige Lösung umfüllen_

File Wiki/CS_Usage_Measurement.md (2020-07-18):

[Deutsche Version dieser Seite](https://github.com/CitizenSensor/CitizenSensor/blob/master/Wiki/CS_Usage_Measurement-DE.md)

# Nitrate Measurement #

## Basic Knowledge for Nitrate Measurement ##

The CitizenSensor device should enable every user to perform a nitrate measurement. To achieve this goal, the software of the CitizenSensor device guides the user through the individual steps of the nitrate measurement process.

Since the basic knowledge of nitrate measurement is contained in the software of the CitizenSensor, no further specialist knowledge is required to carry out the measurement process. The step-by-step instructions ensure that the necessary procedures are followed during the measuring process.

The CitizenSensor instructional software guides the user through four phases of the measurement:

1. Preparation of the measuring electrode
2. Calibration
3. Nitrate measurement
4. Storing the measuring electrode

Please note that the nitrate measuring electrode must be stored in a dry place to avoid damage. For this reason, the measuring electrode must be "released from stock" in step 1 before the measuring process and moistened for some time before the measurement. For the same reason, the measuring electrode must be dried and "transferred to stock" after the measurement in step 4.

In step 2 the CitizenSensor device must be calibrated before measurement. This ensures that the device delivers accurate readings when measuring nitrate.

The actual nitrate measurement takes place in step 3. 

Finally, the nitrate measuring electrode is rinsed in step 4 and stored dry.

Sufficient time should be planned for the entire measurement process - the entire process takes about 2 hours. If several measurements are carried out in succession, it is not necessary to calibrate the CitizenSensor device before each individual measurement.

## Tools and Materials for Nitrate Measurement ##

The following equipment and materials are required for nitrate measurement:

- CitizenSensor device
- Measuring electrode
- Calibration solutions
- Filtered, aqueous solution of the soil sample
- ISA Solution

## Procedure for Nitrate Measurement ##

### Preparation of the Measuring Electrode ###

The nitrate measuring electrode must be stored in a dry place to avoid damage. Immediately before measuring nitrate, however, the measuring electrode must be stored in liquid for some time to prepare it for measurement.

The steps for preparing the nitrate measuring electrode are

1. Releasing the dry measuring electrode from stock
2. Rinsing the measuring electrode with distilled water
3. Storing the measuring electrode in 4ppm calibration solution for two hours

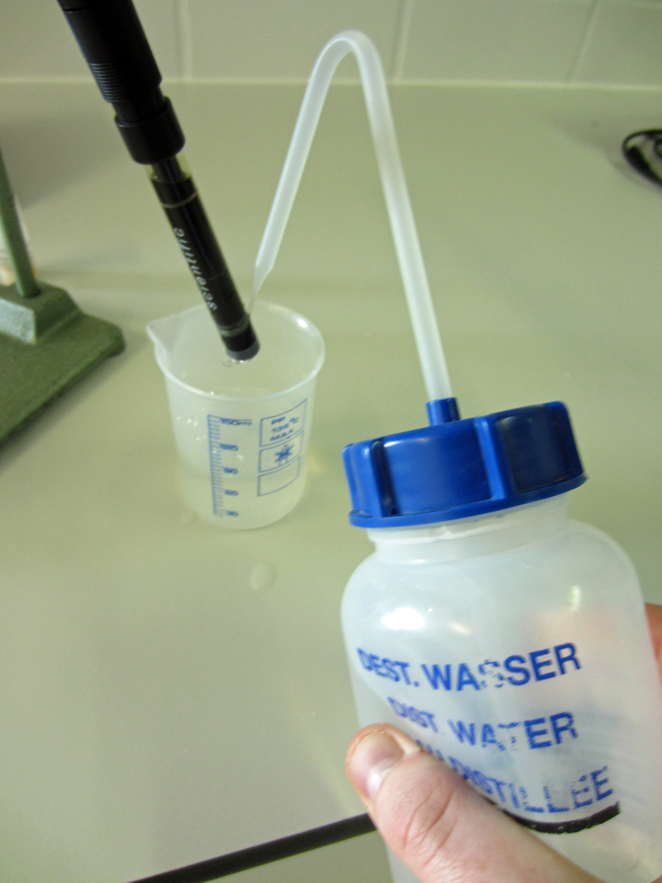
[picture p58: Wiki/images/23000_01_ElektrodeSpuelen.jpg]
Preperation of Measuring Electrode

_Image 1: Preparation of Measuring Electrode_

### Calibration ###

The CitizenSensor device must be calibrated with three differently concentrated calibration liquids (0.1 ppm, 4 ppm and 100 ppm KNO3) before the nitrate measurement.

[Details on preparing the calibration solution](https://github.com/CitizenSensor/CitizenSensor/blob/master/Wiki/CS_Usage_Preparation)

The calibration process ensures that the CitizenSensor device delivers the most accurate readings possible.

To start the calibration, the menu item "Kalibrieren" must be selected on the CitizenSensor device. The device then guides the user through all further calibration steps.

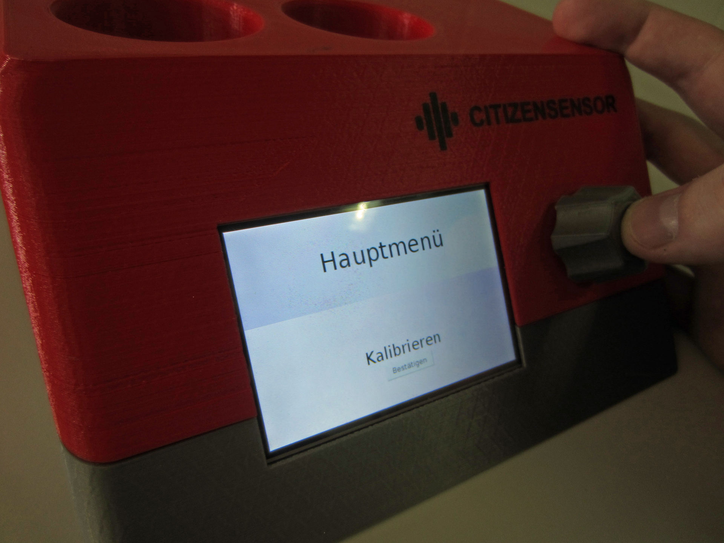
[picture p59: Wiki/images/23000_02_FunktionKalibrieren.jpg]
Function Calibration

_Image 2: Function Calibration_

The individual steps of the calibration are: 
- Select calibration solution
- Rinse the electrode
- Start stirring the calibration liquid
- Measurement of the calibration liquid

## Nitrate Measurement ###

The nitrate measurement is performed with the filtered, aqueous solution of the soil sample. For the measurement, a so-called ion amplifier solution (ISA) must be added to the aqueous solution.

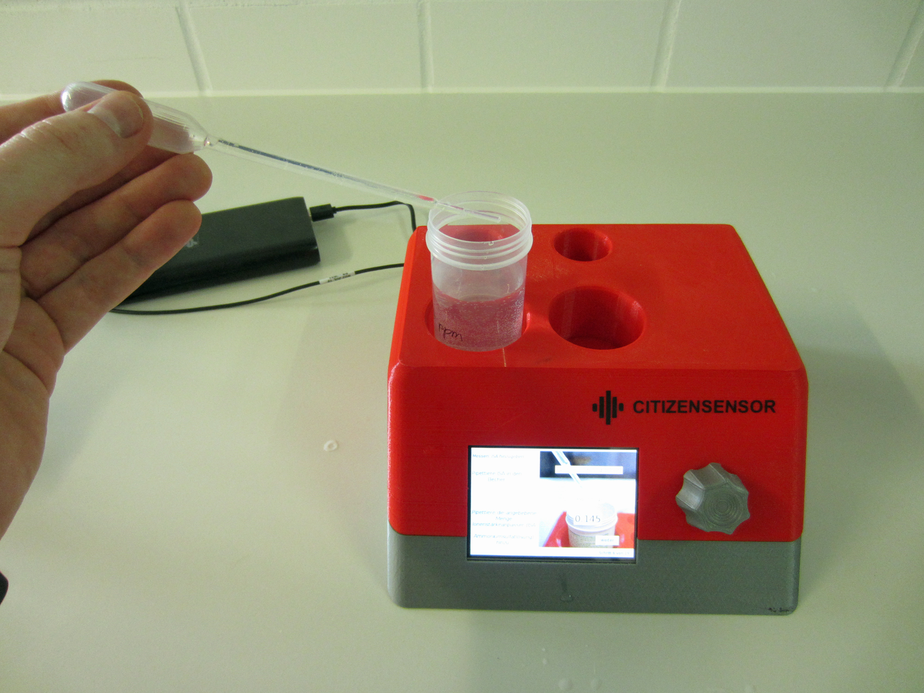
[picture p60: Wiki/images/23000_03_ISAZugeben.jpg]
Adding Ion Amplifier Solution (ISA)

_Image 3: Adding Ion Amplifier Solution (ISA)_

[Details on preparing the ISA solution](https://github.com/CitizenSensor/CitizenSensor/blob/master/Wiki/CS_Usage_Preparation-DE).

To start the nitrate measurement, the menu item "Messen" must be selected on the CitizenSensor device. The device then guides the user through all further steps of the nitrate measurement.

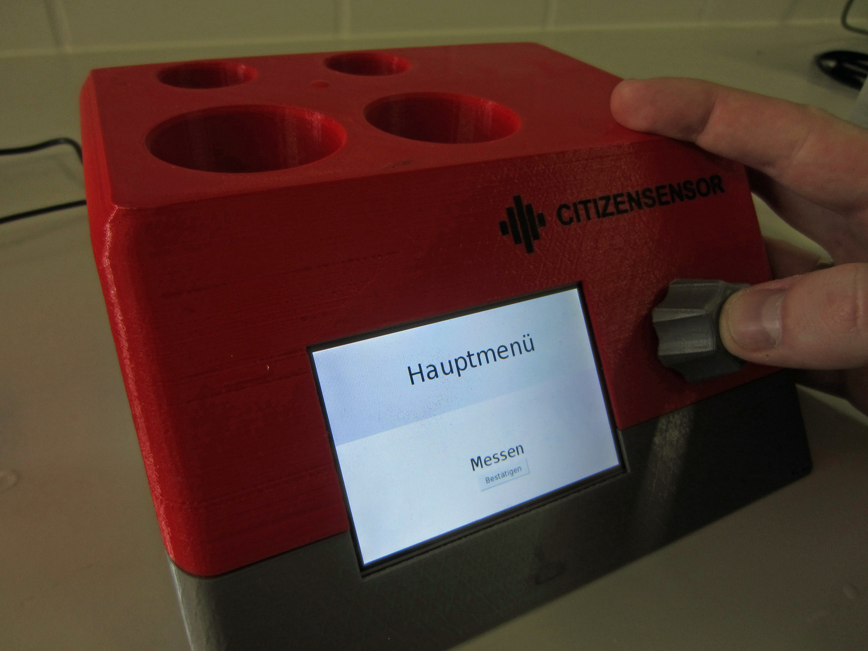
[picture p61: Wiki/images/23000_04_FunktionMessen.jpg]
Function Measurement

_Image 4: Function Measurement_

The individual steps of the nitrate measurement are 
- Calibration of the scale
- Weigh aqueous solution
- Add ISA solution
- Start stirring the aqueous solution
- Nitrate measurement

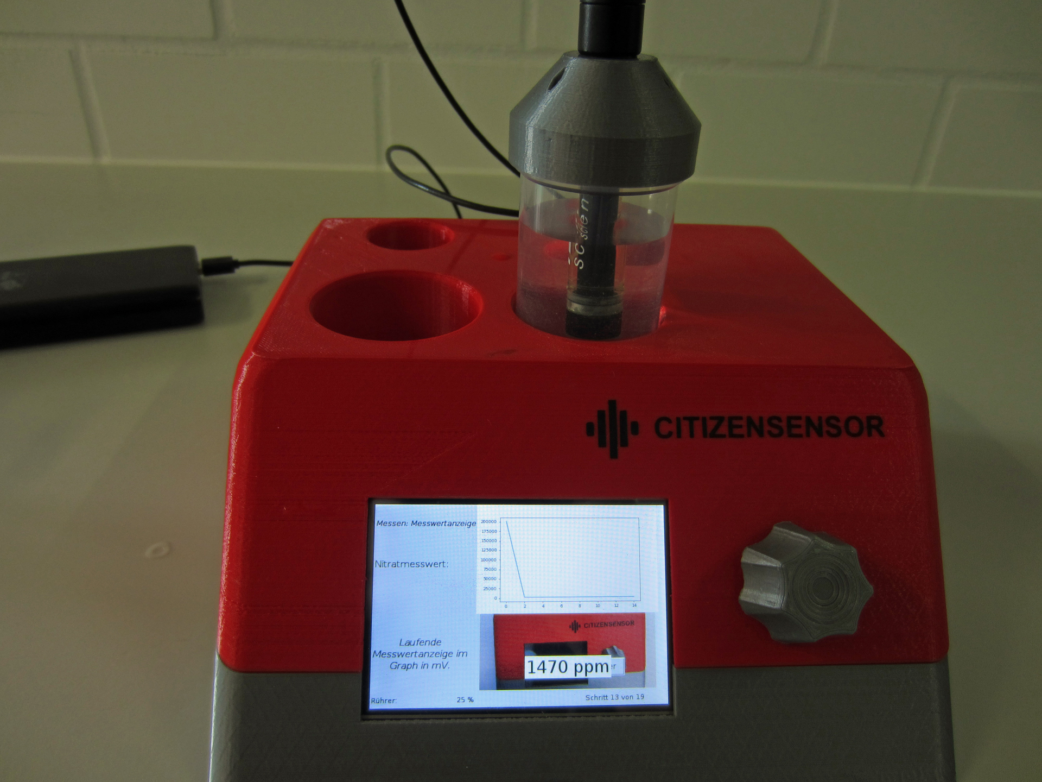
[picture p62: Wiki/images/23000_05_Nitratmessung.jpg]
Nitrate Measurement

_Image 5: Nitrate Measurement_

The final result of the measurement is given by the CitizenSensor device in unit "Nmin". 

### Transferring the measuring electrode to stock ###

After the nitrate measurement, the measuring electrode must be rinsed with distilled water and shaken dry. The electrode can then be stored in a dry place.

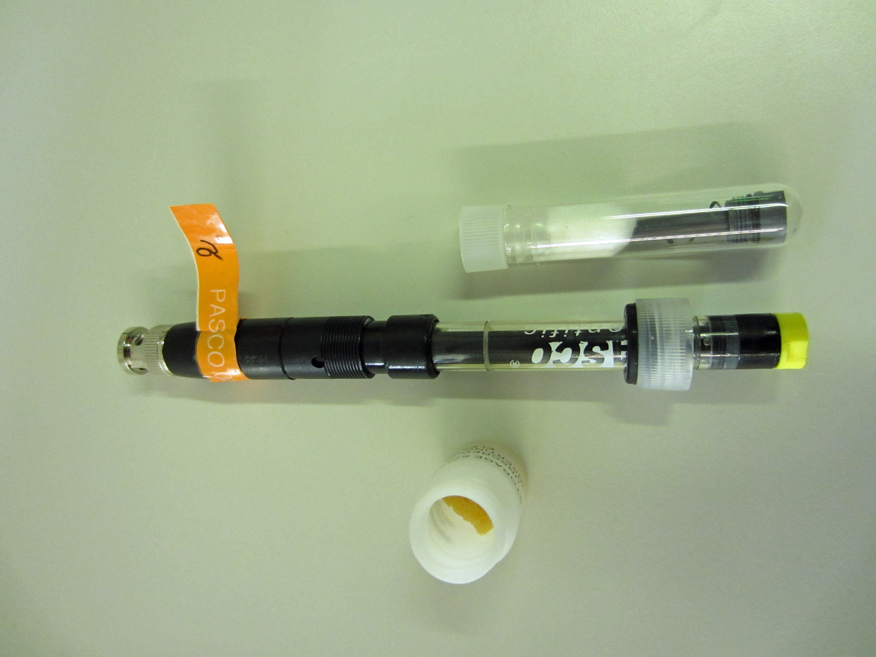
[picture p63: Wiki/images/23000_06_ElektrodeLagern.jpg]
Stored Measuring Electrode

_Image 6: Stored Measuring Electrode_

If further nitrate measurements are planned in the near future, the measuring electrode can also be stored in 4ppm calibration solution for a limited period of time. To avoid damage to the measuring electrode, storage in liquid for more than three days should be avoided.

### Interpretation of the measurement results ###

The CitizenSensor project does not deal with the interpretation of nitrate readings, as this would go beyond the scope of the project. For the evaluation of the measurement results we refer to other sources of information, such as [6]. 

# Further Information (German Only) #
- [06] [Bayerische Landesanstalt für Weinbau und Gartenbau, "Leitfaden für die Düngung im Garten"](http://www.lwg.bayern.de/mam/cms06/gartenakademie/dateien/duengungsbrosch%C3%BCre_bericht_2.pdf)

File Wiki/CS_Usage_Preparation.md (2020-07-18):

[Deutsche Version dieser Seite](https://github.com/CitizenSensor/CitizenSensor/blob/master/Wiki/CS_Usage_Preparation-DE.md)

# Preparation of Nitrate Measurement #

For the nitrate measurement with the CitizenSensor device a number of preparations are necessary. Specifically, several solutions have to be prepared that are needed for the measurement process:

- Calibration fluids 
- Ion amplifier solution (ISA) 

The calibration liquids are required to obtain precise measurement values during nitrate measurement.

The ion amplifier solution (ISA) is required to produce an aqueous solution from the soil sample. The aqueous solution contains the sodium dissolved from the soil sample.

The CitizenSensor device supports the user in the preparation of all these solutions.

# Basic Knowledge about Calibration and Calibration Solutions #

The CitizenSensor device must be calibrated with calibration solutions of varying concentrations before the nitrate measurement. In concrete terms, three calibration solutions with different nitrate concentrations are presented to the measuring instrument.

In the CitizenSensor device, potassium nitrate calibration solutions are used that have a concentration of 100 ppm, 4 ppm, 0.1 ppm and 0.01 ppm NO3-N.

Hints:
- "100 ppm" means, for example, that the solution contains 100 mg of substance per liter
- "100 ppm NO3-N" means that the solution contains 100 mg nitrogen per litre

During calibration, the measuring instrument determines the associated electrical potential (the voltage in millivolts) for each of the calibration solutions and stores this value. For example, the following measured values could result from the calibration:

- 4 ppm: 290 mV
- 100 ppm: 230 mV

Once the CitizenSensor meter is calibrated, the nitrate concentration in aqueously dissolved soil samples can also be measured precisely.
Based on the calibration readings, the CitizenSensor meter can calculate the nitrate concentration of the soil sample by interpolation.

Hint:
The measuring range of the CitizenSensor meter is limited.
A meaningful measurement can only be made in the range 0.1 ppm to 100 ppm NO3-N,
because only in this area there is a linear relationship between nitrate concentration and electrical potential.

# Basic Knowledge of the Ion Amplifier Solution #

The nitrate measurement in the CitizenSensor device is carried out with an ion sensitive electrode. The electrode used is designed for nitrate measurement in liquids. Therefore, an aqueous solution of the soil sample must first be prepared for the measurement. When preparing the aqueous solution, the sodium is dissolved out of the soil sample. 

For the measurement with the CitizenSensor device, the soil sample is not simply dissolved in distilled water. 

Instead, the electrode used requires an "ion strength adjustment solution" (ISA) for optimum measurement results. Specifically, the ISA solution is an ammonium sulfate solution (see [5] page 3).

# Using the Ion Amplifier Solution and Calibration Solutions #

Once the calibration solutions and the ion amplifier solution have been prepared, a nitrate measurement can be performed with their help.

The entire procedure consists of 
- Preparation of an aqueous solution from a soil sample
- Calibration of the CitizenSensor device
- Carrying out the nitrate measurement

The individual steps are:

1. Fill cup with soil
2. Fill cup with distilled water
3. Shake aqueous solution of soil and water
4. Filter aqueous solution
5. Calibrate the CitizenSensor device using the **calibration fluids**.
6. Add **Ion strength adjustment solution (ISA)** to the aqueous solution
7. Stir aqueous solution with ISA
8. Carry out nitrate measurement of the aqueous solution while continuing to stir

## Producing calibration liquids ##

### Tools and Materials for the Production of Calibration Fluids ###

The following tools and materials are required for the production of calibration liquids:

- Potassium nitrate (4 g)
- Plastic cup (200 ml capacity)
- Knife (dosage with knife tip)
- Distilled water: spray bottle with 500 ml

### Production of the Calibration Solutions ###

The production of calibration solutions is triggered on the CitizenSensor device by selecting the menu item "Kalibrierlösung herstellen". The instrument then guides the user through the steps required to prepare the solutions.

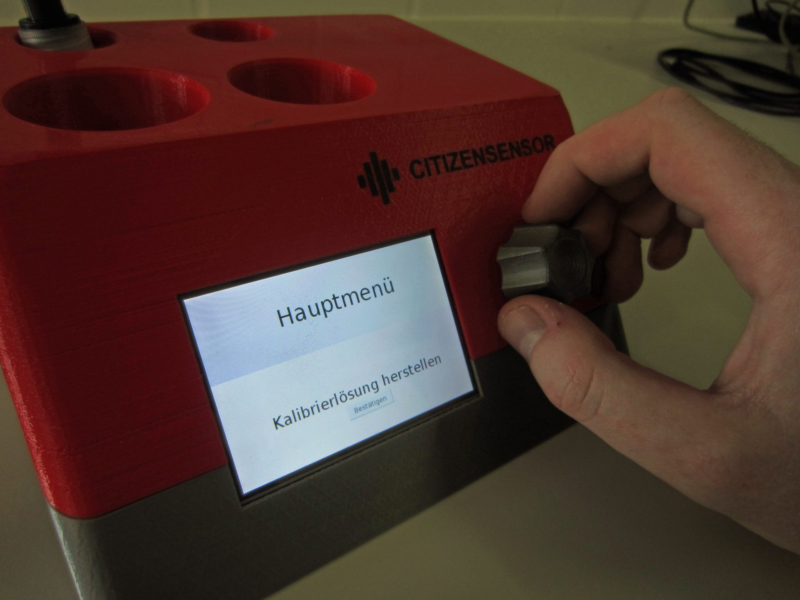
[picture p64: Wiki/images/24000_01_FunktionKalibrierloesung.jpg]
Function Production of Calibration Solutions

_Image 1: Function Production of Calibration Solutions_

The calibration solutions are prepared in two steps. First a stock solution with a concentration of 5000 ppm is prepared. This stock solution is then further diluted to produce solutions with 100 ppm, 4 ppm, 0.1 ppm and 0.01 ppm.

This procedure was chosen because the precision of the integrated scale in the CitizenSensor device is limited. Only a highly concentrated solution of 5000 ppm can be weighed with an acceptable error.

The individual steps in the preparation of the stock solution are: 
- Calibrate the balance
- Weigh in potassium nitrate (3609.3 mg)
- Fill the cup with distilled water (100 ml)
- Stir stock solution
- Label the cup (5000 ppm)

In this way, diluted calibration solutions are produced one after the other.
- **100 ppm calibration solution** is formed from 5000 ppm stock solution (2.08 ml) with 102.03 ml water 
- **4 ppm calibration solution** results from 100 ppm calibration solution (4.11 ml) with 98.64 ml water 
- **0.1 ppm calibration solution** results from 4 ppm calibration solution (2.75 ml) with 107.25 ml water 
- **0.01 ppm calibration solution** results from 0.1 ppm calibration solution (10 ml) with 90 ml water 

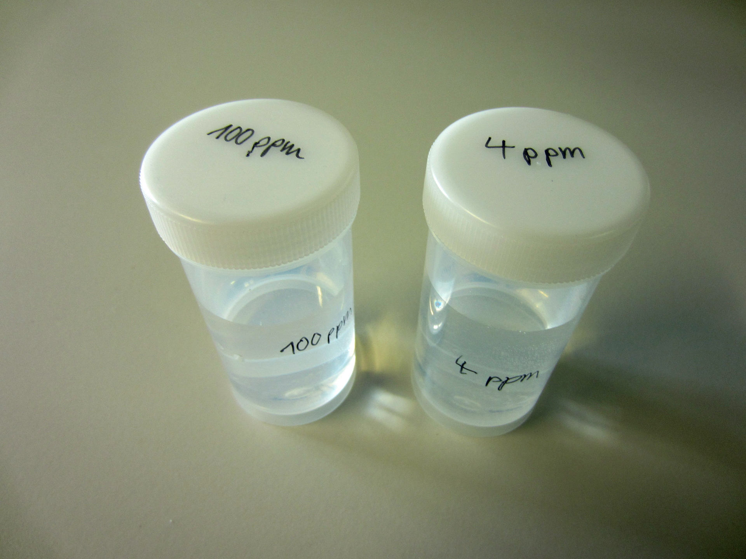
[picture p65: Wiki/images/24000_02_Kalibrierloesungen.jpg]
Calibration Solutions

_Image 2: Calibration Solutions_

## Producing the Ion Aplifier Solution ##

### Tools and Materials for the Preparation of the Ion Amplifier Solution ###

The following tools and materials are required to produce the ion amplifier solution:

- Ammonium sulphate (30 g)
- Plastic cup (200 ml capacity)
- Knife (dosage with knife tip)
- Distilled water: spray bottle with 500 ml

### Production of the Ion Aplifier Solution ###

The production of the ion amplifier solution (ISA) is triggered on the CitizenSensor device by selecting the menu item "ISA herstellen". The device then guides the user through the steps required to prepare the ISA solution.

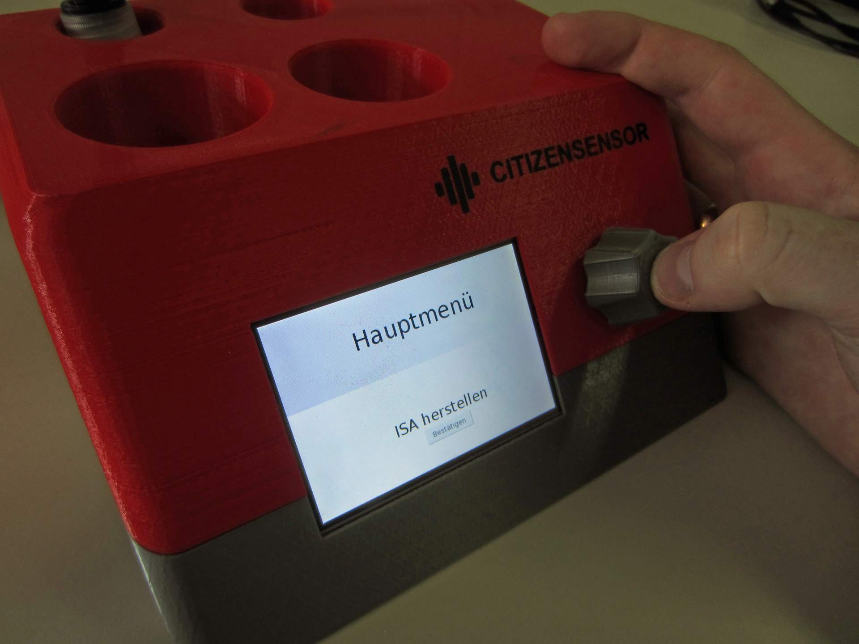
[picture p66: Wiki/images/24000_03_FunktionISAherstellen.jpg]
Function Production of ISA

_Image 3: Function Production of ISA_

The individual steps are: 
- Calibrate the scale
- Weigh out ammonium sulphate
- Fill the cup with distilled water
- Stir ISA solution
- Label the cup

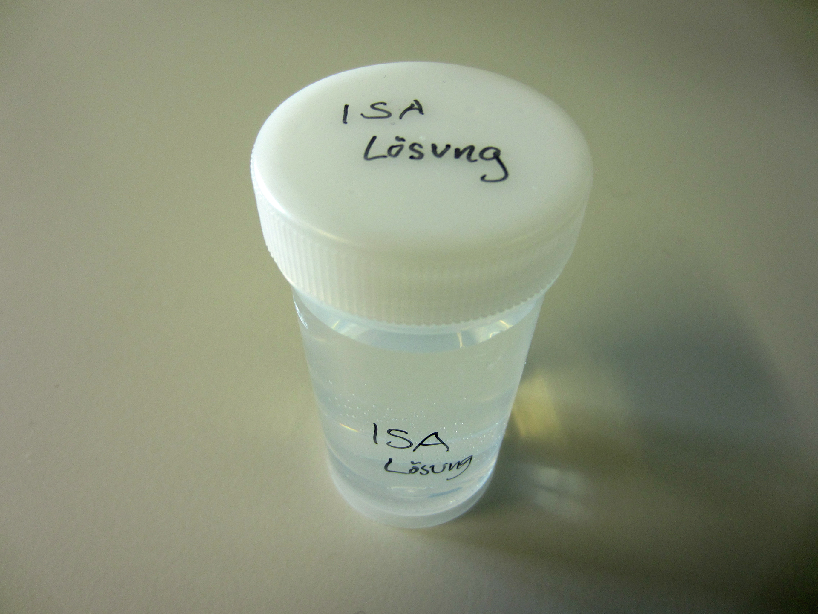
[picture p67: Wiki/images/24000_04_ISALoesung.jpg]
ISA Solution

_Image 4: ISA Solution_

# Further Information #

- [05] [PASCO, Nitrate Ion Selective Electrode CI-6735 Instruction Manual](https://d2n0lz049icia2.cloudfront.net/product_document/Nitrate-Ion-Selective-Electrode-Manual-CI-6735.pdf)

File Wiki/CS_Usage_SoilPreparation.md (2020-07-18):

[Deutsche Version dieser Seite](https://github.com/CitizenSensor/CitizenSensor/blob/master/Wiki/CS_Usage_SoilPreparation-DE.md)

# Soil Preparation #

## Basic Knowledge for Preparation of Soil Samples ##

In the previous step "soil sampling" a total of 2 kg soil was collected. This soil sample is composed of several individual samples, which were taken at different locations and at different depths.

For the nitrate measurement, a representative portion of approx. 100 g soil must now be taken from the total quantity of 2 kg soil. A representative portion can only be obtained if the sample is well mixed beforehand.

The first step is therefore to grind the soil sample, which crushes larger chunks of soil. In this step, larger stones should also be removed from the soil sample. By grinding the soil sample, the sample can then be mixed much better.

In the second step, the quantity of the soil sample is systematically reduced. **Here it is important not to take "any subset" of the soil sample.** In practice, it has been shown that **measuring errors of 10 to 25 percent** occur if the soil sample is mixed and reduced with an unsystematic approach.

For the systematic reduction of the soil sample a sample divider should be used.

If no sample divider is available, it is recommended to reduce the sample size using the "cone and quarter" method (see [04], p. 23/24). This method ensures that an even mixture of larger and smaller soil crumbs is taken.

## Tools and Materials for Preparation of Soil Samples ##

- **Plastic bags with soil samples** (results from step "Soil Sampling")
- **Soil grinder**, **mincer** or fine-mesh **sieve** (5 mm)
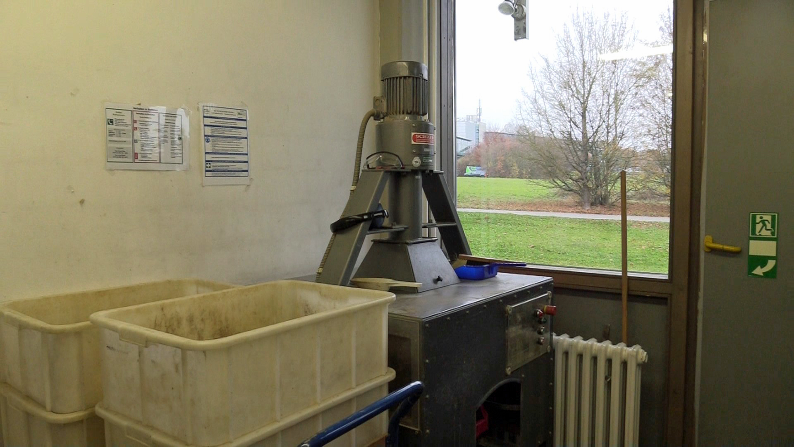
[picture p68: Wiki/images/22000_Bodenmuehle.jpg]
Soil Grinder

_Image 1: Soil Grinder_
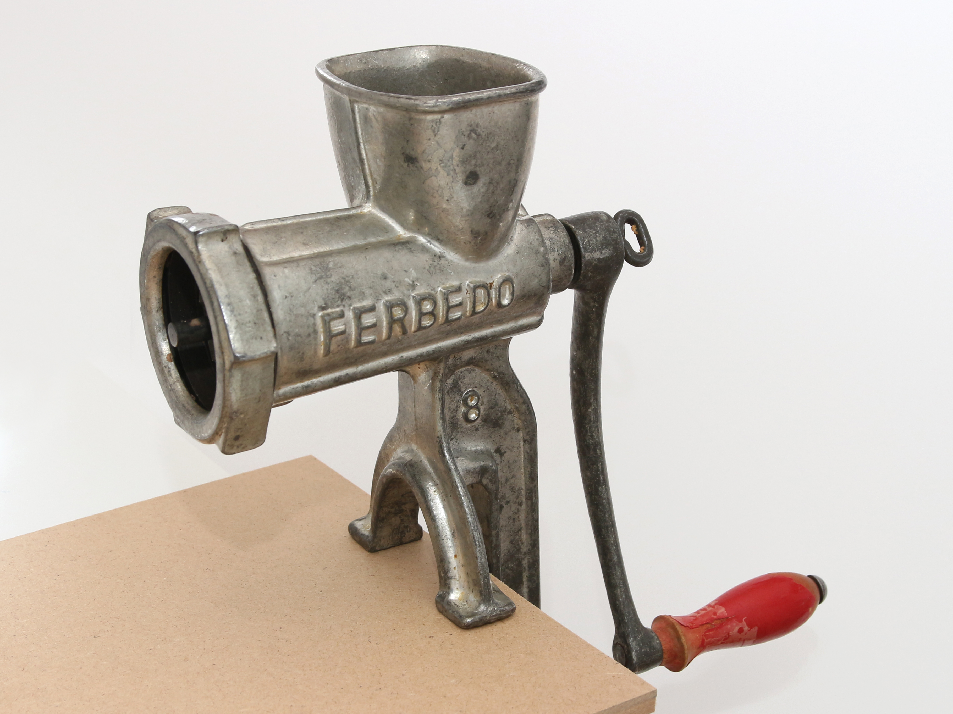
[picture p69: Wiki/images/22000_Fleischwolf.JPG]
Mincer

_Image 2: Mincer_
- **Sample divider** or **thin panel** (plastic or wood)
Sample Divider
_Image 3: Sample Divider_
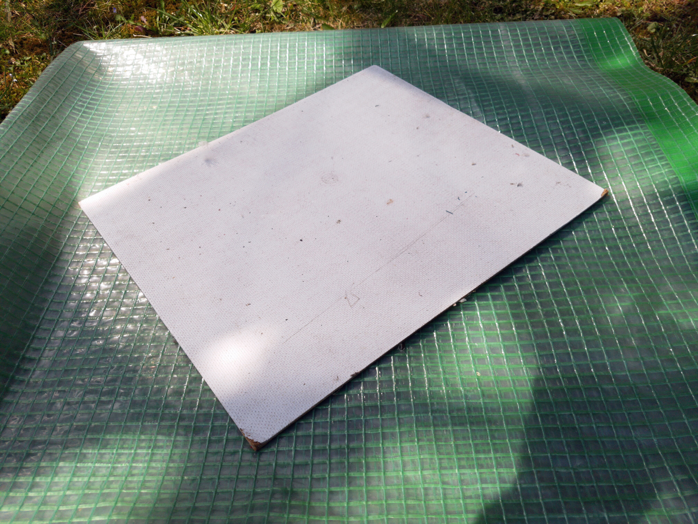
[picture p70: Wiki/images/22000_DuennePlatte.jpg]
Thin Panel

_Image 4: Thin Panel_
- **Small plastic tarp** (1 x 1 meter)
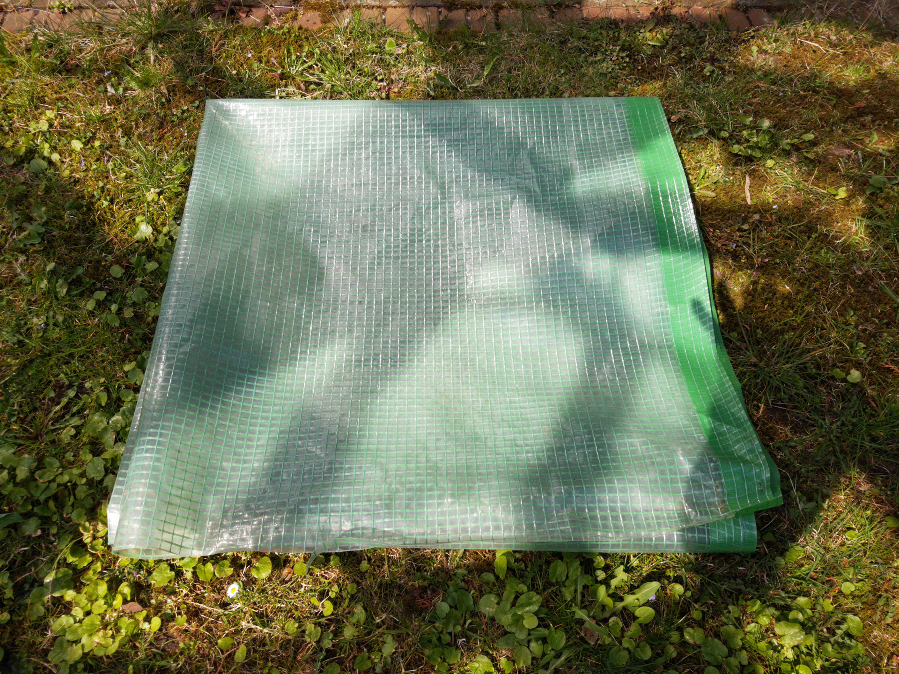
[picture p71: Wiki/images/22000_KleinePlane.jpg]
Plastic Tarp

_Image 5: Plastic Tarp_
- **Small bucket** (5 litres), **garden shovel**, **plastic cup**
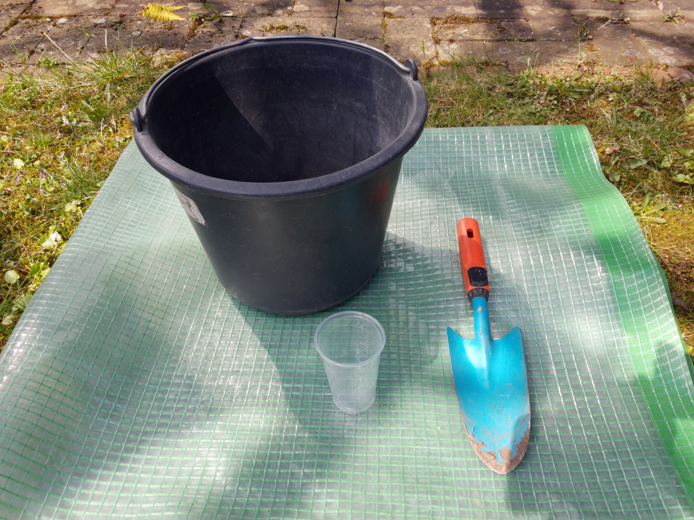
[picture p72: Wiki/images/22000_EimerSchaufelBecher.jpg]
Bucket

_Image 6: Bucket, Garden Shovel, Plastic Cup_

## Procedure for Grinding Soil Samples ##

The soil sample should be ground using a soil mill until crumbs of 5 mm or less are formed.

If a soil mill is not available, the sample should be ground with a mincer or grated through a fine-mesh sieve (5 mm).

## Procedure for Grinding Soil Samples with a Mincer ##

1. **Fill soil sample into small bucket**

2. **Crush larger pieces of soil** in the soil sample by hand
3. **Sort out larger stones in the soil sample** 
The soil sample should only contain stones that are smaller than the distances of the screw conveyor in the mincer - otherwise the mincer could block while turning.

4. **Unscrew the fastening ring of the mincer and remove the perforated disc**.
Fastening Ring
_Image 7: Unscrewed Fastening Ring and removed Perforated Disc_

5. **Grind the soil sample in portions** with the mincer: 
Fill soil sample into the filling funnel of the mincer and grind by cranking. It is recommended to crank with little force. Blockages can be released by alternately cranking forwards and backwards.
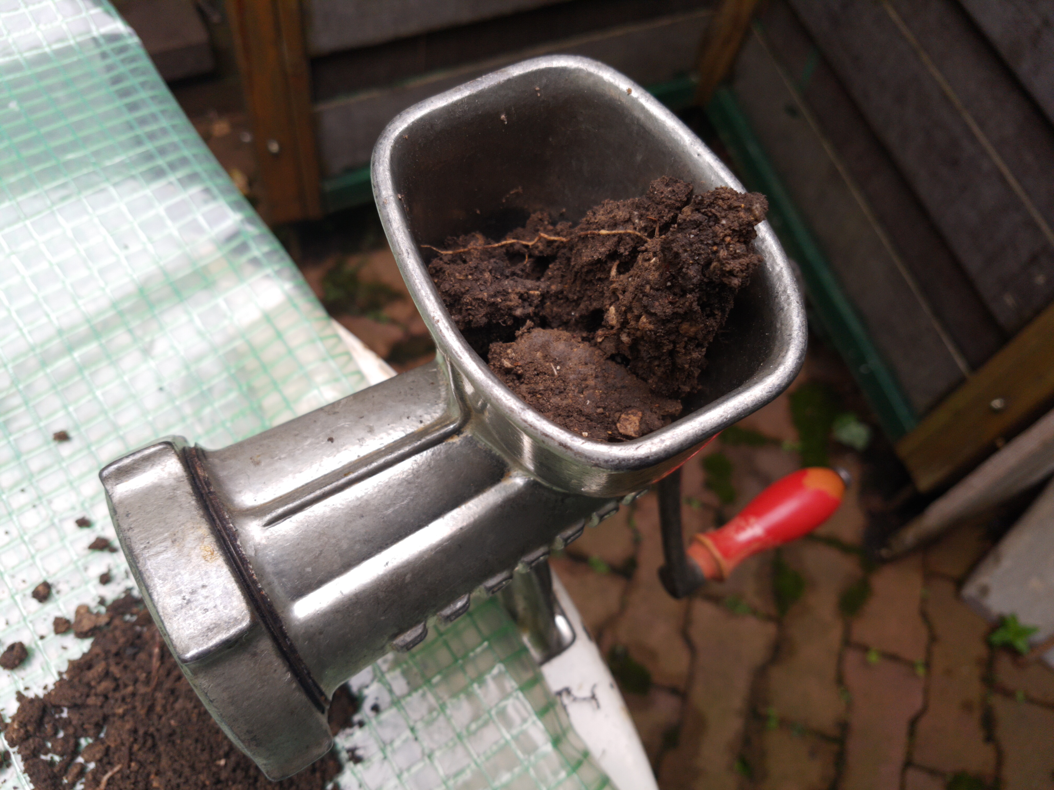
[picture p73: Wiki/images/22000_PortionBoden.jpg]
Grind Soil Sample

_Image 8: Grind Soil Sample_
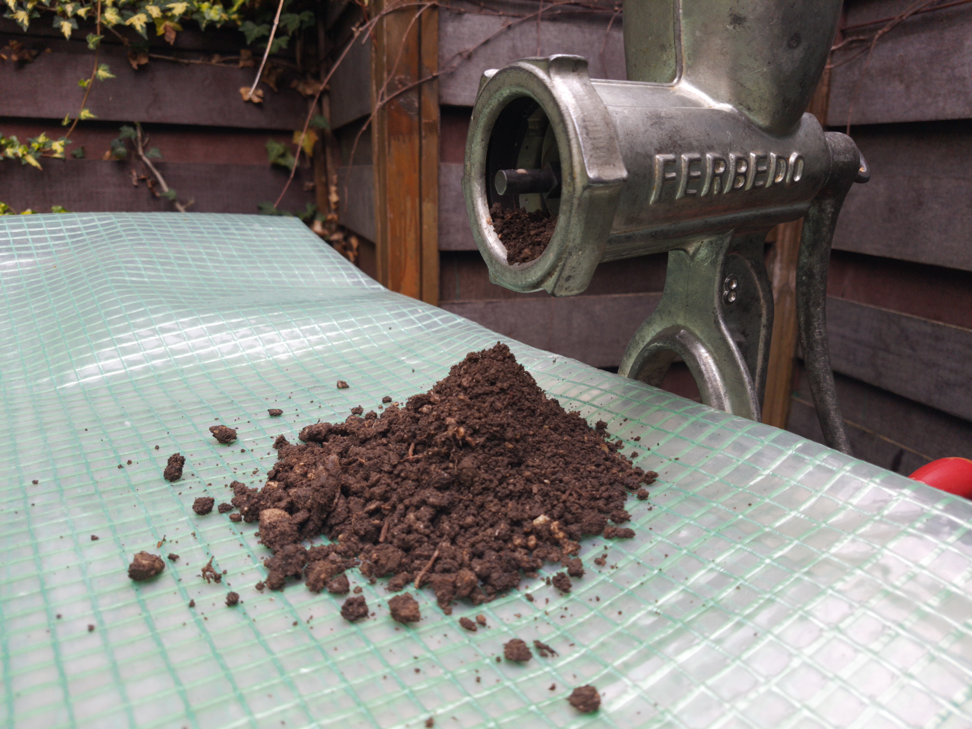
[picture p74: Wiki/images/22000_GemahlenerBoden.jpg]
Ground Soil Sample

_Image 9: Ground Soil Sample_

If the ground soil sample still contains too large chunks of soil, it should be ground with the mincer again. If the grinding with the mincer results in compressed "soil sausages" these can be crumbled very easily with the fingers.

## Procedure for Reducing the Sample Quantity with the Sample Divider ##

1. **Fill the ground sample (2 kg) into the opening of the sample divider:** The two collection containers of the sample divider now each contain half the sample quantity (1 kg).
Fill Sample Divider
_Image 10: Fill Sample Divider with Soil Sample_

2. **Fill reduced sample quantity into the sample divider again**. The halved quantity can now be taken from one of the collecting containers.
Take Halved Soil Sample
_Image 11: Talke Halved Soil Sample_

3. **Repeat step 2 three more times:** halved sample quantities of 500 g, 250 g and 125 g are obtained.

4. **Fill reduced sample quantity (125 g) into plastic cups.**

## Procedure for Reducing the Sample Quantity by "cone and quarter" Method ##

1. **Pour the soil sample (2 kg) into a small soil cone.**
Pour Soil Cone
_Image 12: Pour Soil Cone_

2. **Quarter the soil cone with a thin panel.**
Halve Soil Cone
_Image 13: Halve Soil Cone_
Halved Soil Cone
_Image 14: Halved Soil Cone_
Quater Soil Cone
_Image 15: Quarter Soil Cone_
Quartered Soil Cone
_Image 16: Quartered Soil Cone_

3. **Halve the sample quantity:** the diagonally opposite quarters of the soil cone are removed with a garden shovel.
Halve Sample
_Image 17: Halve the Sample_

4. **Pour the remaining sample amount into a soil cone again:** the remaining soil is shovelled into a bucket, then poured back into a small soil cone.
Fill Half Sample into Bucket
_Image 18: Fill Half Sample into Bucket_
Pour Half Sample
_Image 19: Pour Half Sample into Soil Cone_

5. **Repeat steps 3 and 4 three more times:** this produces halved sample quantities of 500 g, 250 g and finally 125 g.
1000g Sample
_Image 20: 1000g Sample_
500g Sample
_Image 21: 500g Sample_
250g Sample
_Image 22: 250g Sample_

6. **Fill reduced sample quantity (125 g) into plastic cup.**
Cup with Soil Sample
_Image 23: Cup with Soil Sample_

# Further Information (German Only) #

- [04] [Länderarbeitsgemeinschaft Abfall (LAGA), "PN 98 Richtlinie für das Vorgehen bei 
physikalischen, chemischen und biologischen Untersuchungen"](https://www.laga-online.de/documents/m32_laga_pn98_1503993280.pdf)

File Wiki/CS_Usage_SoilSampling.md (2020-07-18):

[Deutsche Version dieser Seite](https://github.com/CitizenSensor/CitizenSensor/blob/master/Wiki/CS_Usage_SoilSampling-DE.md)

# Soil Sampling #

## Basic Knowlegde on Soil Sampling ##

In practice, it has been shown that the biggest measurement errors in nitrate measurement are caused by an incorrect methodology when taking or preparing soil samples.

It is therefore advisable to follow the procedure described below as closely as possible when taking and preparing soil samples.

The recommended procedure aims to produce a homogenised soil sample. Substances like ammonium, nitrate and nitrite are typically not evenly distributed in the soil. If a single soil sample was taken at only one location for the nitrate measurement, the nitrate measurement would result in a rather random nitrate measurement value.

A homogeneous soil sample is achieved by taking several soil samples at different locations (sampling points) and at different depths. For orientation: in agriculture, 15 to 20 samples are typically taken for nitrate measurements [01] [02] [03].

In total, a sample quantity of 2 kg soil should be obtained when taking the soil sample. The individual samples are then carefully mixed in the "sample preparation" step so that a soil sample is obtained in which ammonium, nitrate and nitrite are evenly distributed.

A quantity of 20 g of soil can then be taken from this soil sample for the nitrate measurement. Since the soil sample has been homogenised beforehand, the measured value for the partial quantity of 20 g is representative for the entire sample.

## Tools and Materials for Taking Soil Samples ##

### Three-part Auger ###

Auger
_Image 1: Auger_

The auger should be designed for impact depths of 0-30 cm, 30-60 cm and 60-90 cm. Other designations for the auger are "Nmin drill" (Nmin stands for "N mineral") or "[Pürckhauer (German disgnation)](https://de.wikipedia.org/wiki/P%C3%BCrckhauer)".

### Drop Hammer ###

Drop Hammer
_Image 2: Drop Hammer_

The drop hammer is used to drive the auger into the ground.

### Knife / Screwdriver ###

Screwdriver
_Image 3: Knive or Screwdriver_

A knife or a screwdriver is used to scrape the soil sample out of the auger. When sampling with a spade, a strip is cut out of the soil sample while utilizing a knife.

### Spade ###

Spade
_Image 4: Spade_

If no auger is available for sampling, the soil sample can alternatively be taken with a spade. If an auger and a spade are available, the auger is the preferred tool.

### Labeled Plastic Bags for Soil Samples ###

Plastic Bags
_Image 5: Plastic Bag_

Labelled plastic bags should be kept available for sampling in order to document the origin of the soil samples.

For sampling with an auger, three bags should be labeled per sampling point("0-30", "30-60" and "60-90"). For sampling with a spade, one bag per sampling site is sufficient.

Ideally, the location (e.g. the number of the sampling site) and the date of sampling should also be noted on the bag.

### Cool Box / Cooler Bag ###

Cool Box
_Image 6: Cool Box_

A cool bag or cool box with some cool packs is used to transport the soil sample. 

## Proceedure for Taking Soil Samples ##

First of all, it must be determined at which different locations soil samples should be taken. For this purpose, 15 to 20 sampling points should be determined, whereby these should be distributed as evenly as possible - but randomly - over the area to be measured (see [03] page 9).

The following steps should be carried out at each sampling point:

### Sampling by Auger ###

1. **Treading down the soil at the extraction point:** treading down the soil is only necessary for loose soil. This step is not required for drawing samples from grassland.

2. **Clean the auger:** the auger should be free of soil residues from previous drillings

3. **Hammering in the auger:** the auger is plunged vertically and then hammered in with a drop hammer. For the first sample the auger should be hammered in up to the 30 cm mark. For the further samples the sampling depth is 60 cm or 90 cm.

Plunging the Auger
_Image 7: Plunging the Auger_
Hammering in the Auger
_Image 8: Hammering in the Auger_

4. **Unscrewing the auger:** the auger is unscrewed by pulling upwards.
Unscrewing the Auger
_Image 9: Unscrewing the Auger_

5. **Remove the top layer of soil:** the top 2-3 cm of the soil sample should be removed from the auger. By removing the top layer, it is avoided that the sample is contaminated by soil from the adjacent soil layer.
Remove Top Layer of Soil
_Image 10: Remove Top Layer of Soil_

6. **Scrape out the drill core:** the drill core is scraped out of the auger into the sample bag with a knife / screwdriver.
Scrape out Drill Core
_Bild 11: Scrape out Drill Core_

For further information on sampling with an auger see [01].

### Sampling by spade ###

1. **Dig a hole in the ground at the sampling point:** the hole should be at least as wide and as deep as the blade of the spade.

Digging an Earth Hole
_Image 12: Digging an Earth Hole_

Earth Hole
_Image 13: Earth Hole_

2. **Cutting off a soil slice:** a soil slice is cut off at the edge of the earth hole. The soil sample should be between 20 and 30 cm high and 5 cm thick.

Cut off Soil Slice
_Image 14: Cut off Soil Slice_

Excavate Soil Slice
_Image 15: Excavate the Soil Slice_

3. **Cutting out a bar of soil:** a bar of soil is cut out of the centre of the soil slice. The bar of soil should be approx. 3 cm wide - this results in a bar of soil of 3 cm x 5 cm x 30 cm.

Cut off Bar of Soil
_Image 16: Cutting out Bar of Soil_

4. **Pack soil bar into the sample bag.**

Pack Soil Bar
_Bild 17: Pack Soil Bar_

For further information on sampling by spade see [03].

### Transport and storage of soil samples ###

The soil samples should be cooled down to at least 5 degrees Celsius to inhibit the activity of soil bacteria. If the soil sample is warmed-up to higher temperatures, this will lead to a falsified nitrate measurement value.

If a measurement of the nitrate value cannot be made on the day of the soil sampling, the soil sample should be stored in a freezer until measurement.

# Further Information (German Only) #

- [01] [Bayerische Landesanstalt für Landwirtschaft, Infoblatt "Anleitung zum Ziehen von Nmin-Proben"](https://www.lfl.bayern.de/mam/cms07/iab/dateien/anleitung_ziehen_von_nmin_bodenproben_.pdf)
- [02] [Niedersächsicher Landesbetrieb für Wasserwirtschaft, Küsten- und Naturschutz, Broschüre "Grundwasser Band 8, Untersuchung des mineralischen Stickstoffs im Boden"](https://www.nlwkn.niedersachsen.de/download/69971/NLWKN_2010_Untersuchung_des_mineralischen_Stickstoffs_im_Boden._Empfehlungen_zur_Nutzung_der_Herbst-Nmin-Methode_Band_8_.pdf)
- [03] [Bayerische Gartenakademie, "Leitfaden für die Düngung im Garten"](http://www.lwg.bayern.de/mam/cms06/gartenakademie/dateien/duengungsbrosch%C3%BCre_bericht_2.pdf)

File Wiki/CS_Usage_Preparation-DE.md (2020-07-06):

[English version of this page](https://github.com/CitizenSensor/CitizenSensor/blob/master/Wiki/CS_Usage_Preparation.md)

# Vorbereitungen für die Nitratmessung #

Für die Nitratmessung mit dem CitizenSensor Gerät sind eine Reihe von Vorbereitungen nötig. Konkret müssen mehrere Lösungen hergestellt werden, die bei der Messung gebraucht werden:

- Kalibrierflüssigkeiten 
- Ionenverstärker-Lösung (ISA) 

Die Kalibrierflüssigkeiten sind erforderlich um bei der Nitratmessung präzise Messwerte zu erhalten.

Die Ionenverstärker-Lösung (ISA) wird benötigt um aus der Bodenprobe eine wässrige Lösung herzustellen. Die wässrige Lösung enthält dabei das aus der Bodenprobe herausgelöste Natrium.

Das CitizenSensor Gerät unterstützt den Benutzer bei der Herstellung all dieser Lösungen.

# Grundlagenwissen zu Kalibrierung und Kalibrierlösungen #

Das CitizenSensor Gerät muss vor der Nitratmessung mit unterschiedlich stark konzentrierten Kalibrierlösungen kalibriert werden. Konkret werden dem Messgerät dabei drei Kalibrierlösungen mit unterschiedlicher Nitratkonzentration präsentiert.

Beim CitizenSensor Messgerät werden Kaliumnitrat-Kalibrierlösungen (Kalisalpeter) eingesetzt, die eine Konzentration von 100 ppm, 4 ppm, 0.1 ppm und 0.01 ppm NO3-N haben.

Hinweise:
- "100 ppm" bedeutet dabei zum Beispiel, dass die Lösung 100 mg Substanz pro Liter enthält
- "100 ppm NO3-N" bedeutet, dass die Lösung 100 mg Stickstoff pro Liter enthält

Bei der Kalibrierung ermittelt das Messgerät für jede der Kalibrierlösungen das zugehörige elektrische Potential (die Spannung in Millivolt), und speichert diesen Wert ab. Zum Beispiel könnten sich bei der Kalibrierung folgende Messwerte ergeben:

- 4 ppm: 290 mV
- 100 ppm: 230 mV

Sobald das CitizenSensor Messgerät kalibriert ist, kann auch die Nitratkonzentration in wässrig gelösten Bodenproben präzise gemessen werden.
Anhand der Messwerte der Kalibrierung kann das CitizenSensor Messgerät die Nitratkonzentration der Bodenprobe durch Interpolation berechnen.

Hinweis:
Der Messbereich des CitizenSensor Messgeräts ist beschränkt.
Eine sinnvolle Messung kann nur im Bereich 0.1 ppm bis 100 ppm NO3-N erfolgen,
da nur in diesem Bereich ein linearer Zusammenhang zwischen Nitratkonzentration und elektrischem Potential besteht.

# Grundlagenwissen zur Ionenverstärker-Lösung #

Die Nitratmessung wird beim CitizenSensor Gerät mit einer ionensensitiven Elektrode durchgeführt. Die verwendete Elektrode ist für Nitratmessung in Flüssigkeiten ausgelegt. Für die Messung muss daher zunächst eine wässrige Lösung der Bodenprobe hergestellt werden. Beim Herstellen der wässrigen Lösung wird das Natrium aus der Bodenprobe herausgelöst. 

Für die Messung mit dem CitizenSensor Gerät, wird die Bodenprobe nicht einfach in destilliertem Wasser gelöst. 

Die eingesetzte Elektrode erfordert stattdessen für optimale Messergebnisse eine  "Ionenstärke-Adjustierlösung" (ISA). Konkret handelt es sich bei der ISA-Lösung um eine Ammoniumsulfatlösung (siehe [5] Seite 3).

# Verwendung der Ionenverstärker-Lösung und der Kalibrierlösungen #

Sobald die Kalibrierlösungen und die Ionenverstärker-Lösung hergestellt wurden, kann mit deren Hilfe eine Nitratmessung erfolgen.

Der gesamte Ablauf besteht aus 
- Herstellung einer wässrigen Lösung aus einer Bodenprobe
- Kalibrierung des CitizenSensor-Geräts
- Durchführung der Nitratmessung

Die Einzelnen Schritte sind:

1. Becher mit Erde befüllen
2. Becher mit destilliertem Wasser auffüllen
3. Wässrige Lösung aus Erde und Wasser schütteln
4. Wässrige Lösung filtrieren
5. CitizenSensor-Gerät mit Hilfe der **Kalibrierflüssigkeiten** kalibrieren
6. **Ionenstärke-Adjustierlösung (ISA)** zur wässrigen Lösung hinzugeben
7. Wässrige Lösung mit ISA rühren
8. Nitratmessung der wässrigen Lösung unter weiterem Rühren durchführen

## Kalibrierflüssigkeiten herstellen ##

### Werkzeug und Materialien für die Herstellung der Kalibrierflüssigkeiten ###

Für die Herstellung der Kalibrierflüssigkeiten werden folgende Werkzeuge und Materialien benötigt:

- Kaliumnitrat (4 g)
- Plastikbecher (200 ml Fassungsvermögen)
- Messer (Dosierung mit Messerspitze)
- Destilliertes Wasser: Spritzflasche mit 500 ml

### Herstellung der Kalibrierlösungen ###

Die Herstellung der Kalibrierlösungen wird am CitizenSensor Gerät durch Auswahl des Menüpunkts "Kalibrierlösung herstellen" ausgewählt. Das Gerät führt dann den Benutzer durch die Schritte, die für die Herstellung der Lösungen erforderlich sind.

Funktion Kalibrierlösung erstellen
_Bild 1: Funktion Kalibrierlösung erstellen_

Die Herstellung der Kalibrierlösungen erfolgt in zwei Schritten. Zunächst wird eine Stammlösung der Konzentration 5000 ppm hergestellt. Diese Stammlösung wird dann weiter verdünnt, so dass Lösungen mit 100 ppm, 4 ppm, 0.1 ppm und 0.01 ppm entstehen.

Diese Vorgehensweise wurde gewählt, weil die Präzision der Wägezelle im CitizenSensor Gerät begrenzt ist. Nur eine hochkonzentrierte Lösung von 5000 ppm kann mit vertretbarem Fehler abgewogen werden.

Die Einzelschritte bei der Herstellung der Stammlösung sind: 
- Waage kalibrieren
- Kaliumnitrat einwiegen (3609.3 mg)
- Becher mit destilliertem Wasser auffüllen (100 ml)
- Stammlösung rühren
- Becher beschriften (5000 ppm)

Die Einzelschritte bei der Herstellung der verdünnten Kalibrierungslösungen sind: 
- Waage kalibrieren
- Kaliumnitrat-Lösung einwiegen 
- Lösung durch Einfüllen von destilliertem Wasser verdünnen
- Kalibrierlösung rühren
- Becher beschriften

Auf diese Art entstehen der Reihe nach immer weiter verdünnte Kalibrierungslösungen.
- **100 ppm Kalibrierlösung** entsteht aus 5000 ppm Stammlösung (2.08 ml) mit 102.03 ml Wasser 
- **4 ppm Kalibrierlösung** entsteht aus 100 ppm Kalibrierlösung (4.11 ml) mit 98.64 ml Wasser 
- **0.1 ppm Kalibrierlösung** entsteht aus 4 ppm Kalibrierlösung (2.75 ml) mit 107.25 ml Wasser 
- **0.01 ppm Kalibrierlösung** entsteht aus 0.1 ppm Kalibrierlösung (10 ml) mit 90 ml Wasser 

Kalibrierlösungen
_Bild 2: Fertige Kalibrierlösungen_

## Ionenverstärker-Lösung herstellen ##

### Werkzeug und Materialien für die Herstellung der Ionenverstärker-Lösung ###

Für die Herstellung der Ionenverstärker-Lösung werden folgende Werkzeuge und Materialien benötigt:

- Ammoniumsulfat (30 g)
- Plastikbecher (200 ml Fassungsvermögen)
- Messer (Dosierung mit Messerspitze)
- Destilliertes Wasser: Spritzflasche mit 500 ml

### Herstellung der Ionenverstärker-Lösung ###

Die Herstellung der Ionenverstärker-Lösung (ISA) wird am CitizenSensor Gerät durch Auswahl des Menüpunkts "ISA herstellen" ausgewählt. Das Gerät führt dann den Benutzer durch die Schritte, die für die Herstellung der ISA-Lösung erforderlich sind.

Funktion ISA herstellen
_Bild 3: Funktion ISA herstellen_

Die Einzelschritte sind: 
- Waage kalibrieren
- Ammoniumsulfat einwiegen
- Becher mit destilliertem Wasser auffüllen
- ISA-Lösung rühren
- ISA-Lösung beschriften

ISA Lösung
_Bild 4: Fertige ISA Lösung_

# Weiterführende Informationen #

- [05] [PASCO, Nitrate Ion Selective Electrode CI-6735 Instruction Manual](https://d2n0lz049icia2.cloudfront.net/product_document/Nitrate-Ion-Selective-Electrode-Manual-CI-6735.pdf)

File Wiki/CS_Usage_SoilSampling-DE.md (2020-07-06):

[English version of this page](https://github.com/CitizenSensor/CitizenSensor/blob/master/Wiki/CS_Usage_SoilSampling.md)

# Probennahme #

## Grundlagenwissen zur Entnahme von Bodenproben ##

In der Praxis hat sich gezeigt, dass die größten Messfehler bei der Nitrat-Messung durch eine falsche Methodik bei der Entnahme von Bodenproben oder bei der Vorbereitung von Bodenproben entstehen.

Für die Entnahme und Vorbereitung von Bodenproben empfiehlt es sich daher, die unten beschriebene Vorgehensweise möglichst exakt zu befolgen.

Die empfohlene Vorgehensweise zielt darauf ab, dass am Ende eine homogenisierte Bodenprobe entsteht. Stoffe wie Ammonium, Nitrat und Nitrit sind typischerweise nicht gleichmäßig im Boden verteilt. Würde man für die Nitrat-Messung eine einzelnen Bodenprobe, an nur einem Ort entnehmen, so würde der Nitrat-Messwert zu einem eher zufälligen Messwert führen.

Eine homogene Bodenprobe erreicht man dadurch, dass man im ersten Schritt mehrere Bodenproben an verschiedenen Orten (Einstichstellen), und in verschiedenen Tiefen entnimmt. Zur Orientierung: in der Landwirtschaft werden für die Nitrat-Messung typischerweise 15 bis 20 Proben entnommen [01] [02] [03].

Insgesamt sollte bei der Entnahme der Bodenprobe eine Probenmenge von insgesamt 2 kg Boden entstehen. Die einzelnen Proben werden dann im Schritt  "Probenaufbereitung" sorgfältig durchmischt, so dass sich eine Bodenprobe ergibt, in der Stoffe Ammonium, Nitrat und Nitrit gleichmäßig verteilt sind.

Aus dieser Bodenprobe kann dann für die Nitrat-Messung eine Menge von 20 g Boden entnommen werden. Da die Bodenprobe zuvor homogenisiert wurde, ist der Messwert für die Teilmenge von 20 g repräsentativ für die gesamte Probe.

## Werkzeug und Materialien für die Entnahme von Bodenproben ##

### Dreiteiliger Bohrstock ###

Bohrstock
_Bild 1: Bohrstock_

Der Bohrstock sollte für die Einschlagtiefen 0-30 cm, 30-60 cm und 60-90 cm ausgelegt sein. Andere Bezeichnung für den Bohrstock sind "Nmin Bohrer" (Nmin steht für "N mineralisch") oder "[Pürckhauer](https://de.wikipedia.org/wiki/P%C3%BCrckhauer)".

### Schlaghammer ###

Schlaghammer
_Bild 2: Schlaghammer_

Der Schlaghammer dient zum Einschlagen des Bohrstocks in den Boden.

### Messer / Schraubendreher ###

Schraubendreher
_Bild 3: Schraubendreher_

Ein Messer bzw. ein Schraubendreher dienen zum Auskratzen der Bodenprobe aus dem Bohrstock. Bei der Probennahme per Spaten wird mit Hilfe eines Messers ein Streifen aus der Bodenprobe herausgeschnitten. 

### Spaten ###

Spaten
_Bild 4: Spaten_

Steht für die Probennahme kein Bohrstock zur Verfügung, so kann die Bodenprobe alternativ auch mit einem Spaten entnommen werden. Stehen Bohrstock und Spaten zu Verfügung, dann ist der Bohrstock das bevorzugte Werkzeug.    

### Beschriftbare Kunststoffbeutel für Bodenproben ###

Kunststoffbeutel
_Bild 5: Kunststoffbeutel_

Für die Probennahme sollten beschriftbare Kunststoffbeutel bereitgehalten werden, um den Ursprung der Bodenproben zu dokumentieren.

Für die Probennahme mit dem Bohrstock sollten pro Einstichstelle drei Beutel beschriftet werden: "0-30", "30-60" und "60-90". Für die Probennahme per Spaten reicht ein Beutel pro Einstichstelle. 

Idealerweise sollten auch der Ort (z.B. die Nummer der Einstichstelle) und das Datum der Probennahme auf dem Beutel notiert werden.

### Kühltasche / Kühlbox ### 

Kühltasche
_Bild 6: Kühlbox_

Eine Kühltasche oder Kühlbox mit einigen Kühlakkus dient zum Transport der Bodenprobe.

## Vorgehensweise zur Entnahme von Bodenproben ##

Zunächst muss festgelegt werden, an welchen verschiedenen Stellen Bodenproben entnommen werden sollen.  Es sollten dabei 15 bis 20 Entnahmestellen festgelegt werden, wobei diese möglichst gleichmäßig - aber zufällig - über die zu vermessende Fläche verteilt sein sollten (siehe [03] Seite 9).

An jedem Entnahmeort sollten folgende Schritte durchgeführt werden:

### Entnahme per Bohrstock ###

1. **Boden an der Entnahmestelle festtreten:** das Festtreten des Bodens ist nur erforderlich, falls es sich um lockere Erde, und nicht um Rasen handelt.

2. **Bohrstock säubern:** der Bohrstock er sollte frei von Bodenresten aus vorherigen Bohrungen sein

3. **Bohrstock einschlagen:** der Bohrstock wird senkrecht eingestochen, und dann mit dem Schlaghammer eingeschlagen. Bei der ersten Entnahme sollte der Bohrstock bis zur 30 cm Markierung eingeschlagen werden. Bei den weiteren Entnahmen beträgt die Einschlagtiefe 60 cm bzw. 90 cm
Bohrstock einstechen
_Bild 7: Bohrstock einstechen_
Bohrstock einschlagen
_Bild 8: Bohrstock einschlagen_

4. **Bohrstock herausdrehen:** der Bohrstock wird mit Zug nach oben herausgedreht.
Bohrstock herausdrehen
_Bild 9: Bohrstock herausdrehen_

5. **Oberste Erdschicht entfernen:** die obersten 2-3 cm Bodenprobe sollten aus dem Bohrstock entfernt werden. Durch das Entfernen der obersten Schicht wird vermieden, dass die Probe durch Boden aus der angrenzenden Bodenschicht verfälscht wird.
Erdschicht entfernen
_Bild 10: Erdschicht entfernen_

6. **Bohrkern auskratzen:** der Borhkern wird mit einem Messer / Schraubendreher aus dem Bohrstock in den Probenbeutel ausgekratzt.
Bohrkern auskratzen
_Bild 11: Bohrkern auskratzen_

Weitere Informationen zur Entnahme per Bohrstock: siehe [01]. 

### Entnahme per Spaten ###

1. **Erdloch an der Entnahmestelle ausheben:** das Loch sollte mindestens so breit und so tief sein wie das Blatt des Spatens.

Erdloch ausheben
_Bild 12: Erdloch ausheben_

Erdloch
_Bild 13: Erdloch ausheben_

2. **Erdscheibe abstechen:** am Rand des Erdlochs wird eine Erdscheibe abgestochen. Die abgestochene Erdprobe sollte zwischen 20 und 30 cm hoch und 5 cm dick sein.

Erdscheibe abstechen
_Bild 14: Erdscheibe abstechen_

Erdscheibe ausheben
_Bild 15: Erdscheibe ausheben_

3. **Erdstreifen herausschneiden:** ein Streifen Erde wird mittig aus der Erdscheibe herausgeschnitten. Der Erdstreifen sollte ca 3 cm breit sein - es ergibt sich ein Streifen Erde von 3 cm x 5 cm x 30 cm.

Erdstreifen herausschneiden
_Bild 16: Erdstreifen herausschneiden_

4. **Erdstreifen in den Probenbeutel verpacken.**

Erdstreifen verpacken
_Bild 17: Erdstreifen verpacken_

Weitere Informationen zur Entnahme per Spaten: siehe [03]. 

### Transport und Lagerung von Bodenproben ###

Die Bodenproben sollten mindestens bis auf 5 Grad Celsius abgekühlt werden, um die Aktivität der Bodenbakterien zu hemmen. Erwärmt sich die Bodenprobe auf höhere Temperaturen, so wird dies zu einem verfälschten Nitrat-Messwert führen.

Falls eine Messung des Nitrat-Wertes nicht am Tag der Bodenprobe erfolgen kann, dann sollte die Bodenprobe bis zur Messung in der Tiefkühltruhe gelagert werden.

# Weiterführende Informationen #
- [01] [Bayerische Landesanstalt für Landwirtschaft, Infoblatt "Anleitung zum Ziehen von Nmin-Proben"](https://www.lfl.bayern.de/mam/cms07/iab/dateien/anleitung_ziehen_von_nmin_bodenproben_.pdf)
- [02] [Niedersächsicher Landesbetrieb für Wasserwirtschaft, Küsten- und Naturschutz, Broschüre "Grundwasser Band 8, Untersuchung des mineralischen Stickstoffs im Boden"](https://www.nlwkn.niedersachsen.de/download/69971/NLWKN_2010_Untersuchung_des_mineralischen_Stickstoffs_im_Boden._Empfehlungen_zur_Nutzung_der_Herbst-Nmin-Methode_Band_8_.pdf)
- [03] [Bayerische Gartenakademie, "Leitfaden für die Düngung im Garten"](http://www.lwg.bayern.de/mam/cms06/gartenakademie/dateien/duengungsbrosch%C3%BCre_bericht_2.pdf)

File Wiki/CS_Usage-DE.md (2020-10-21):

[English version of this page](https://github.com/CitizenSensor/CitizenSensor/blob/master/Wiki/CS_Usage.md)

# CitizenSensor Bedienung #

Das CitizenSensor Gerät ermöglicht die Messung von Nitrat im Boden. Das Messgerät arbeitet dabei mit einem elektrochemischen Sensor, der den Nitratgehalt in  wässrigen Lösungen bestimmen kann.

Für eine Nitratmessung im Boden müssen daher zunächst einige Schritte durchlaufen werden, um aus einer Bodenprobe eine wässrige Lösung herzustellen.

Die Genaugigkeit des Nitrat-Messwertes hängt stark davon ab, wie sorgfältig bei der Entnahme und der Aufbereitung der Bodenprobe vorgegangen wird.

Wir empfehlen daher die Hinweise in den nachfolgenden Anleitungen möglichst genau zu befolgen.

1. [Probennahme](https://github.com/CitizenSensor/CitizenSensor/blob/master/Wiki/CS_Usage_SoilSampling-DE.md)
2. [Probenaufbereitung](https://github.com/CitizenSensor/CitizenSensor/blob/master/Wiki/CS_Usage_SoilPreparation-DE.md)
3. [Herstellung Wässrige Lösung](https://github.com/CitizenSensor/CitizenSensor/blob/master/Wiki/CS_Usage_AqueousSolution-DE.md)
4. [Vorbereitungen für die Nitratmessung](https://github.com/CitizenSensor/CitizenSensor/blob/master/Wiki/CS_Usage_Preparation-DE.md)
5. [Nitratmessung](https://github.com/CitizenSensor/CitizenSensor/blob/master/Wiki/CS_Usage_Measurement-DE.md)
6. [Interpretation der Messwerte](https://github.com/CitizenSensor/CitizenSensor/blob/master/Wiki/CS_Usage_Interpretation-DE.md)

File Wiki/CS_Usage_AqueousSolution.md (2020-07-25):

[Deutsche Version dieser Seite](https://github.com/CitizenSensor/CitizenSensor/blob/master/Wiki/CS_Usage_AqueousSolution-DE.md)

# Creation of Aqueous Solution #

Text to come

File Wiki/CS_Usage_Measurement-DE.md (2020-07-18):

[English version of this page](https://github.com/CitizenSensor/CitizenSensor/blob/master/Wiki/CS_Usage_Measurement.md)

# Nitratmessung #

## Grundlagenwissen zur Nitratmessung ##

Das CitizenSensor Gerät soll jeden Benutzer in die Lage versetzen eine Nitratmessung durchzuführen. Um dieses Ziel zu erreichen, führt die Software des CitizenSensor Geräts durch die einzelnen Schritte des Nitrat-Messvorgangs.

Da das Grundlagenwissen zur Nitratmessung in der Software des CitizenSensor steckt, ist somit für die Durchführung des Messvorgangs kein weiteres Fachwissen erforderlich. Durch die Schritt-für-Schritt Anleitungen wird sichgergestellt, dass beim Messvorgang die erforderlichen Abläufe befolgt werden.

Die CitizenSensor Anleitungssoftware führt den Benutzer bei der Messung durch vier Phasen:

1. Vorbereitung der Messelektrode
2. Kalibrierung
3. Nitratmessung
4. Einlagern der Messelektrode

Bei der Nitrat-Messelektrode ist zu beachten, dass sie trocken gelagert werden muss, um Beschädigungen zu vermeiden. Aus diesem Grund muss die Messelektrode in Schritt 1 vor dem Messvorgang "ausgelagert" werden und vor der Messung einige Zeit befeuchtet werden. Aus dem gleichen Grund muss die Messelektrode nach der Messung in Schritt 4 wieder trocken "eingelagert" werden.

In Schritt 2 muss das CitizenSensor Gerät vor der Messung kalibriert werden. Damit wird sichergestellt, dass das Gerät bei der Nitratmessung präzise Messwerte liefert.

Die eigentliche Nitratmessung erfolgt in Schritt 3. 

Abschließend wird die Nitrat-Messelektrode in Schritt 4 gespült und trocken eingelagert.

Für den gesamten Messvorgang sollte ausreichend Zeit eingeplant werden - der gesamte Prozess dauert etwa 2 Stunden. Werden mehrere Messungen hintereinander durchgeführt, dann ist es nicht erforderlich das Gerät vor jeder einzelnen Messung zu kalibrieren.

## Werkzeug und Materialien für die Nitratmessung ##

Für die Nitratmessung werden folgende Geräte und Materialien benötigt:

- CitizenSensor Gerät
- Messelektrode
- Kalibrierlösungen
- Filtrierte, wässrige Lösung der Bodenprobe
- ISA Lösung

## Vorgehensweise bei der Nitratmessung ##

### Vorbereitung der Messelektrode ###

Die Nitrat-Messelektrode muss trocken gelagert werden, um Beschädigungen zu vermeiden. Unmittelbar vor der Nitratmessung muss die Messelektrode jedoch einige Zeit feucht gelagert werden, um sie für die Messung vorzubereiten.

Die Schritte zur Vorbereitung der Nitrat-Messelektrode sind

1. Auslagern der trockenen Messelektrode
2. Spülen der Messelektrode mit destilliertem Wasser
3. Lagerung der Messelektrode in 4ppm Kalibrierlösung für zwei Stunden

Messelektrode vorbereiten
_Bild 1: Messelektrode vorbereiten_

### Kalibrierung ###

Das CitizenSensor Gerät muss vor der Nitratmessung mit drei unterschiedlich stark konzentrierten Kalibrierflüssigkeiten (0.1 ppm 4 ppm und 100 ppm KNO3) kalibriert werden.

[Details zur Herstellung der Kalibrierlösung](https://github.com/CitizenSensor/CitizenSensor/blob/master/Wiki/CS_Usage_Preparation-DE)

Durch den Kalibriervorgang wird sichergestellt dass das CitizenSensor Gerät möglichst präzise Messwerte liefert.

Um die Kalibrierung zu starten, muss am CitizenSensor Gerät der Menüpunkt "Kalibrieren" ausgewählt werden. Das Gerät führt dann den Benutzer durch alle weiteren Kalibrierungsschritte.

Funktion Kalibrierung
_Bild 2: Funktion Kalibrierung_

Die Einzelschritte der Kalibrierung sind: 
- Kalibrierlösung wählen
- Elektrode spülen
- Rühren der Kalibrierflüssigkeit starten
- Messung der Kalibrierflüssigkeit

### Nitratmessung ###

Die Nitratmessung wird mit der filtrierten, wässrigen Lösung der Bodenprobe durchgeführt. Für die Messung muss zur wässrigen Lösung eine sogenannte Ionenverstärker-Lösung (ISA) hinzugegeben werden.

Ionenverstärker-Lösung (ISA) zugeben
_Bild 3: Ionenverstärker-Lösung (ISA) zugeben_

[Details zur Herstellung der ISA Lösung](https://github.com/CitizenSensor/CitizenSensor/blob/master/Wiki/CS_Usage_Preparation-DE).

Um die Nitratmessung zu starten, muss am CitizenSensor Gerät der Menüpunkt "Messen" ausgewählt werden. Das Gerät führt dann den Benutzer durch alle weiteren Schritte der Nitratmessung.

Funktion Nitratmessung
_Bild 4: Funktion Messen_

Die Einzelschritte der Nitratmessung sind: 
- Kalibrierung der Waage
- Wässrige Lösung abwiegen
- ISA-Lösung hinzugeben
- Rühren der wässrigen Lösung starten
- Nitratmessung

Nitratmessung
_Bild 5: Nitratmessung_

Das Endergebnis der Messung wird vom CitizenSensor Gerät in der Einheit "Nmin" angegeben. 

### Einlagern der Messelektrode ###

Nach der Nitratmessung muss die Messelektrode mit destilliertem Wasser abgespült und trockengeschüttelt werden. Danach kann die Elektrode trocken eingelagert werden.

Messelektrode einlagern
_Bild 6: Eingelagerte Messelektrode_

Falls weitere Nitratmessungen in näherer Zukunft geplant sind, kann die Messelektrode auch eine beschränkte Zeit feucht in 4ppm Kalibrierlösung gelagert werden. Um Schäden an der Messelektrode zu vermeiden, sollte eine feuchte Lagerung von mehr als drei Tagen vermieden werden.

### Interpretation der Messergebnisse ###

Das Projekt CitizenSensor befasst sich nicht mit der Interpretation der Nitrat-Messwerte, da das den Rahmen des Projektes sprengen würde. Für die Auswertung der Messergebnisse verweisen wir auf andere Informationsquellen, wie zum Beispiel [6]. 

# Weiterführende Informationen #

- [06] [Bayerische Landesanstalt für Weinbau und Gartenbau, "Leitfaden für die Düngung im Garten"](http://www.lwg.bayern.de/mam/cms06/gartenakademie/dateien/duengungsbrosch%C3%BCre_bericht_2.pdf)

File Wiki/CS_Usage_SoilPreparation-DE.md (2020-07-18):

[English version of this page](https://github.com/CitizenSensor/CitizenSensor/blob/master/Wiki/CS_Usage_SoilPreparation.md)

# Probenaufbereitung #

## Grundlagenwissen zur Aufbereitung von Bodenproben ##

Im vorangehenden Schritt "Probennahme" wurde eine Probenmenge von insgesamt 2 kg Boden gesammelt. Diese Bodenprobe setzt sich aus mehreren Einzelproben zusammen, die an verschiedenen Stellen, und in verschiedenen Tiefen entnommen wurden.

Für die Nitrat-Messung muss nun eine repräsentative Teilmenge von ca. 100 g aus den 2 kg Boden entnommen werden. Eine repräsentative Teilmenge ergibt sich nur dann, wenn die Probe gut durchmischt ist.

Der erste Schritt ist daher das Mahlen der Bodenprobe, wodurch größere Erdbrocken zerkleinert werden. In diesem Schritt sollten auch größere Steine aus der Bodenprobe entfernt werden. Durch das Mahlen der Bodenprobe kann die Probe anschließend deutlich besser durchmischt werden.

Im zweiten Schritt wird die Menge der gemahlenen Bodenprobe systematisch reduziert. **Hierbei ist es wichtig, nicht "irgendeine Teilmenge" der Bodenprobe zu entnehmen.** In der Praxis hat sich gezeigt, dass **Messfehler von 10 bis 25 Prozent** entstehen, wenn bei der Durchmischung und Verringerung der Bodenprobe ohne Systematik gearbeitet wird.

Für die systematische Reduzierung der Bodenprobe sollte ein Probenteiler / Riffelteiler
verwendet werden.

Steht kein Probenteiler zur Verfügung, so empfiehlt sich die Reduzierung des Probenumfangs mit der Methode "Kegeln und Vierteln" (siehe hierzu [04], S. 23/24). Diese Methode stellt sicher, dass eine gleichmäßige Mischung aus größeren und kleineren Bodenkrümeln entnommen wird.

## Werkzeug und Materialien für die Aufbereitung von Bodenproben ##

- **Kunststoffbeutel mit Bodenproben** (Ergebnisse aus Schritt "Probennahme")
- **Bodenmühle**, **Fleischwolf** oder feinmaschiges **Sieb** (5 mm)
Bodenmühle
_Bild 1: Bodenmühle_
Fleischwolf
_Bild 2: Fleischwolf_
- **Probenteiler / Riffelteiler** oder **dünne Platte** (Kunststoff oder Holz)
Probenteiler/Riffelteiler
_Bild 3: Probenteiler/Riffelteiler_
Dünne Platte
_Bild 4: Dünne Platte_
- **Kleine Plane** (1 x 1 Meter)
Plane
_Bild 5: Plane_
- **Kleiner Eimer (5 Liter), Gartenschaufel, Plastikbecher**
Eimer
_Bild 6: Eimer, Gartenschaufel, Plastikbecher_

## Vorgehensweise zur Mahlen von Bodenproben ##

Die Bodenprobe sollte mit Hilfe einer Bodenmühle so lange gemahlen werden, bis Krümel von 5 mm oder weniger entstehen.

Steht keine Bodenmühle zur Verfügung, so sollte die Probe durch einen Fleischwolf gedreht, oder durch ein feinmaschiges Sieb (5 mm) gerieben werden.

## Vorgehensweise zum Mahlen von Bodenproben mit einem Fleischwolf ##

1. **Bodenprobe in kleinen Eimer füllen**

2. **Größere Erdbrocken in der Bodenprobe mit der Hand zerdrücken**

3. **Größere Steine in der Bodenprobe aussortieren**
In der Bodenprobe sollten nur Steine enthalten sein, die kleiner sind als die Abstände der Förderschnecke im Fleischwolf - andernfalls könnte der Fleischwolf beim Drehen blockieren.

4. **Befestigungsring des Fleischwolfs abschrauben und Lochscheibe entfernen**.
Befestigungsring
_Bild 7: Abgeschraubter Befestigungsring, und entfernte Lochscheibe_

5. **Bodenprobe portionsweise mit dem Fleischwolf durchdrehen:** 
Bodenprobe in den Einfülltrichter des Fleischwolfs einfüllen und durch Kurbeln zerkleinern.
Es empfiehlt sich mit wenig Kraft zu kurbeln. Blockaden können gelöst werden, indem im Wechsel vorwärts und rückwärts gekurbelt wird.
Bodenprobe durchdrehen
_Bild 8: Bodenprobe durchdrehen_
Gemahlene Bodenprobe
_Bild 9: Gemahlene Bodenprobe_

Falls die gemahlene Bodenprobe noch zu große Erdbrocken enthält, sollte sie nochmals durch den Fleischwolf gedreht werden. Falls durch das Mahlen mit dem Fleischwolf zusammengepresste "Erdwürstchen" entstehen, können diese sehr einfach mit den Fingern zerbröselt werden.

## Vorgehensweise zur Reduktion der Probenmenge mit dem Probenteiler ## 

1. **Gemahlene Probe (2 kg) in die Öffnung des Probenteilers einfüllen:** Die beiden Auffangbehältern des Probenteilers enthalten nun jeweils die Halbe Probenmenge (1 kg).
Probenteiler Einfüllen
_Bild 10: Probe in Probenteiler einfüllen_

2. **Reduzierte Probenmenge nochmals in den Probenteiler einfüllen.** Die halbierte Menge kann nun aus einem der Auffangbehälter entnommen werden.
Probenteiler Entnahme
_Bild 11: Probe aus Probenteiler entnehmen_

3. **Schritt 2 noch dreimal wiederholen:** es entstehen halbierte Probenmengen von 500 g, 250 g und 125 g.

4. **Reduzierte Probenmenge (125 g) in Plastikbecher abfüllen.**

## Vorgehensweise zur Reduktion der Probenmenge per "Kegeln und Vierteln" ## 

1. **Gemahlene Probe (2 kg) zu einem kleinen Erdkegel aufschütten.**
Erdkegel aufschütten
_Bild 12: Erdkegel aufschütten_

2. **Erdkegel mit dünner Platte vierteln.**
Erdkegel halbieren
_Bild 13: Erdkegel halbieren_
Halbierter Erdkegel
_Bild 14: Halbierter Erdkegel_
Erdkegel vierterln
_Bild 15: Erdkegel vierteln_
Geviertelter Erdkegel
_Bild 16: Geviertelter Erdkegel_

3. **Probenmenge halbieren:** die diagonal gegenüberliegenden Viertel des Erdkegels werden mit einer Gartenschaufel entfernt.
Probenmenge halbieren
_Bild 17: Probenmenge halbieren_

4. **Restliche Probenmenge neu aufschütten:** Die verbleibende Erde wird in einen Eimer geschaufelt, danach wieder zu einem kleinen Erdkegel aufgeschüttet.
Halbe Probe umfüllen
_Bild 18: Halbe Probe umfüllen_
Halbe Probe aufschütten
_Bild 19: Halbe Probe aufschütten_

5. **Schritte 3 und 4 noch dreimal wiederholen:** so entstehen halbierte Probenmengen von 500 g, 250 g und schließlich 125 g.
1000g Probe
_Bild 20: 1000g Probe_
500g Probe
_Bild 21: 500g Probe_
250g Probe
_Bild 22: 250g Probe_

6. **Reduzierte Probenmenge (125 g) in Plastikbecher abfüllen.**
Becher mit Bodenprobe
_Bild 23: Becher mit Bodenprobe_

# Weiterführende Informationen #

- [04] [Länderarbeitsgemeinschaft Abfall (LAGA), "PN 98 Richtlinie für das Vorgehen bei 
physikalischen, chemischen und biologischen Untersuchungen"](https://www.laga-online.de/documents/m32_laga_pn98_1503993280.pdf)

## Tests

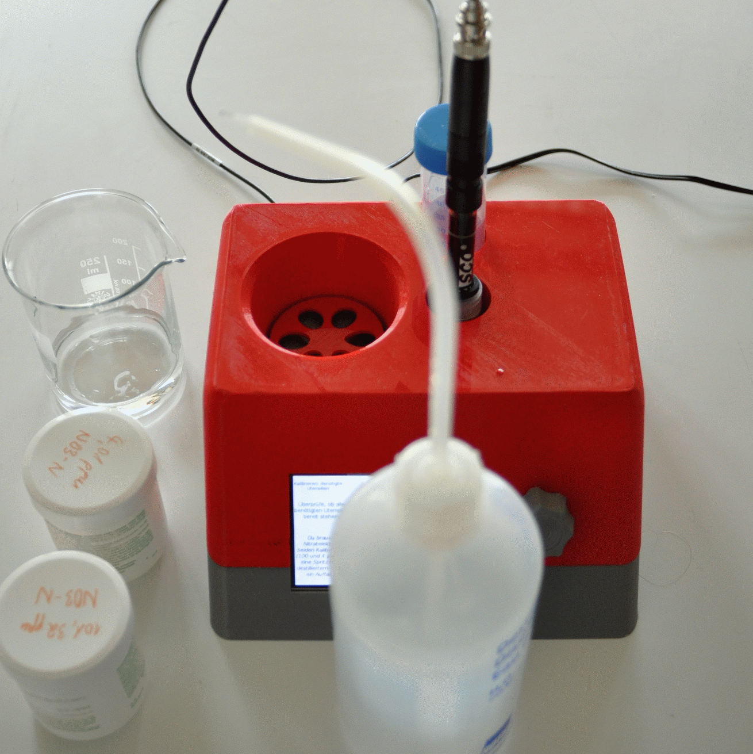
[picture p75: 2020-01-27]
2_Software/photos/kalibrieren_utensilien.gif

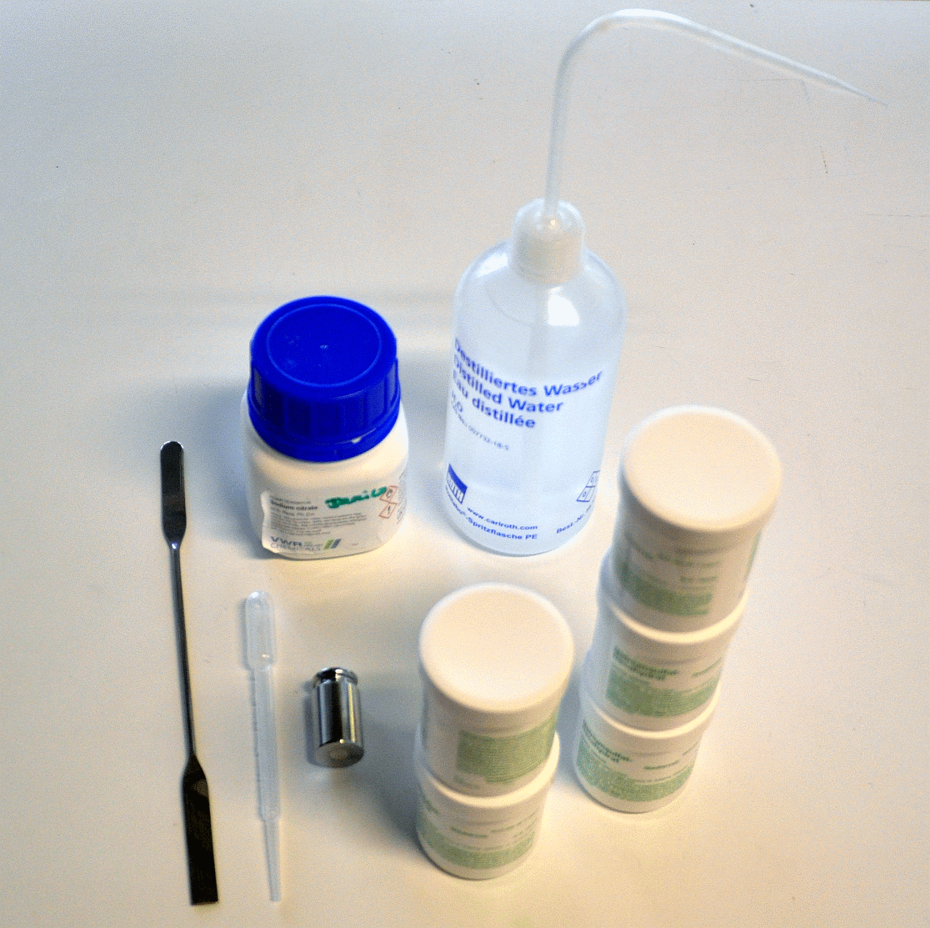
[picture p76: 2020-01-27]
2_Software/photos/kalibrierlösung_utensilien.gif

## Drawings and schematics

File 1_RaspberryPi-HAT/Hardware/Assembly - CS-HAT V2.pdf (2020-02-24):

## TESTPLUG2MM

## PCI-E-36SLOT

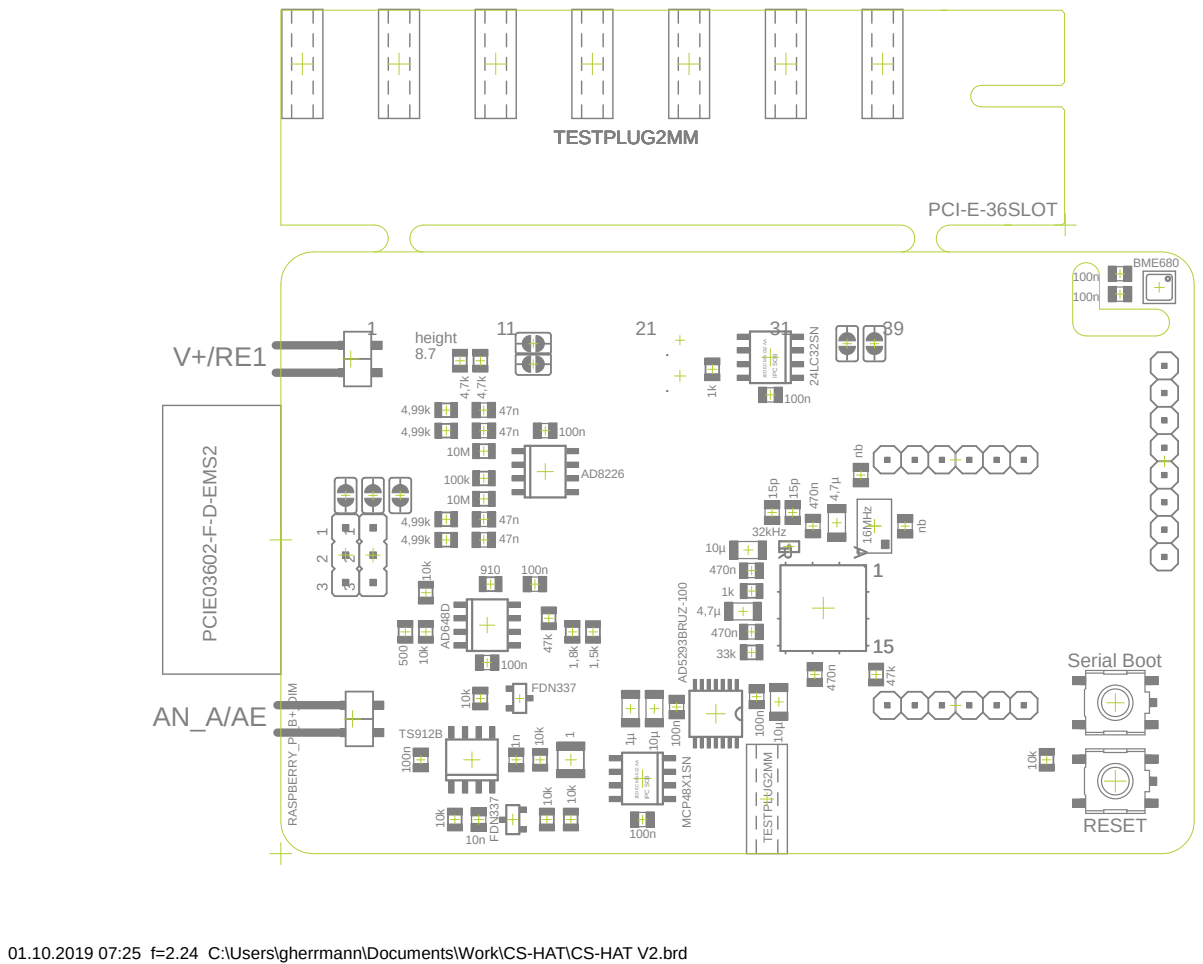
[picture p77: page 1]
BME680; TESTPLUG2MM; height 8.7; RASPBERRY_PI_B+_DIM; 16MHz 32kHz; Serial Boot; RESET; FDN337; PCIE03602-F-D-EMS2 AD8226 100k 10M 10M; MCP48X1SN AD5293BRUZ-100; IPC SO8

JEDEC MS-012 AA

01.10.2019 07:25 f=2.24 C:\Users\gherrmann\Documents\Work\CS-HAT\CS-HAT V2.brd

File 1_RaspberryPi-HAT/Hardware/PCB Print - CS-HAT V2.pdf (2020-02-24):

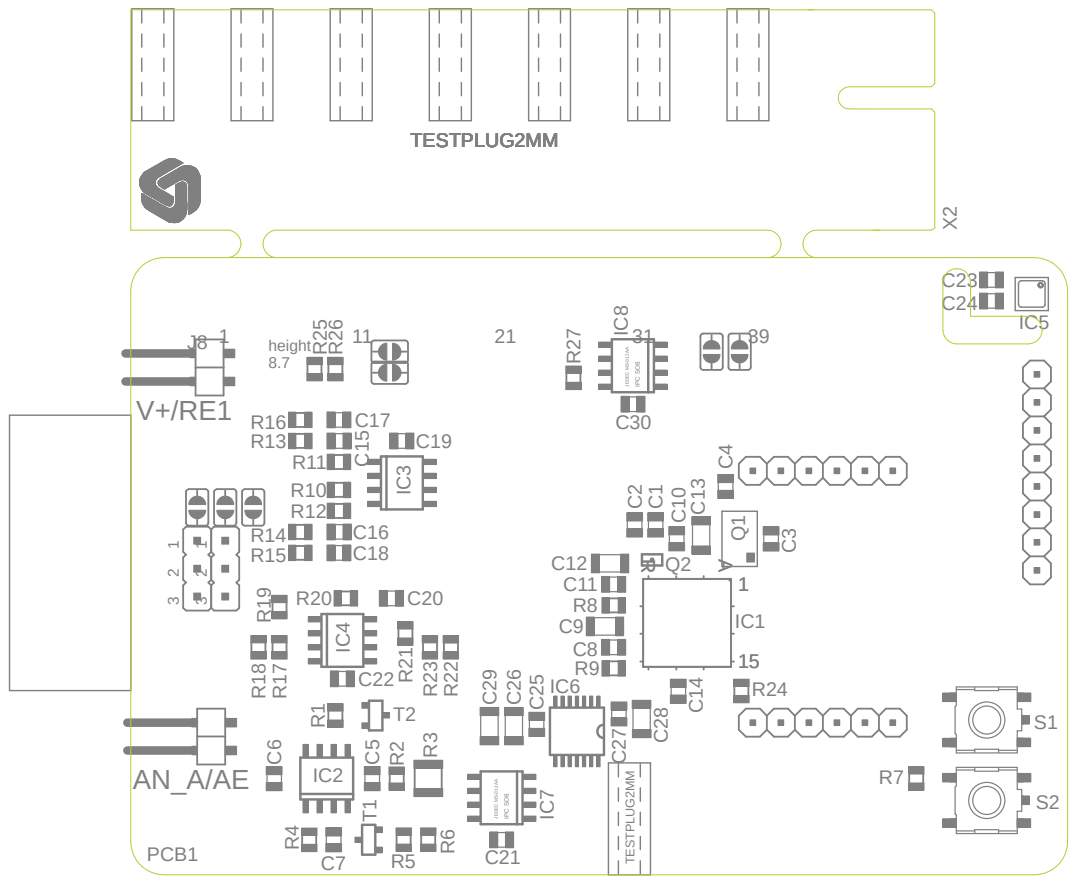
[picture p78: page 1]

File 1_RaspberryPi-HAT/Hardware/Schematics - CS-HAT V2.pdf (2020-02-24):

## ADUCM350BBCZ

## IC1A

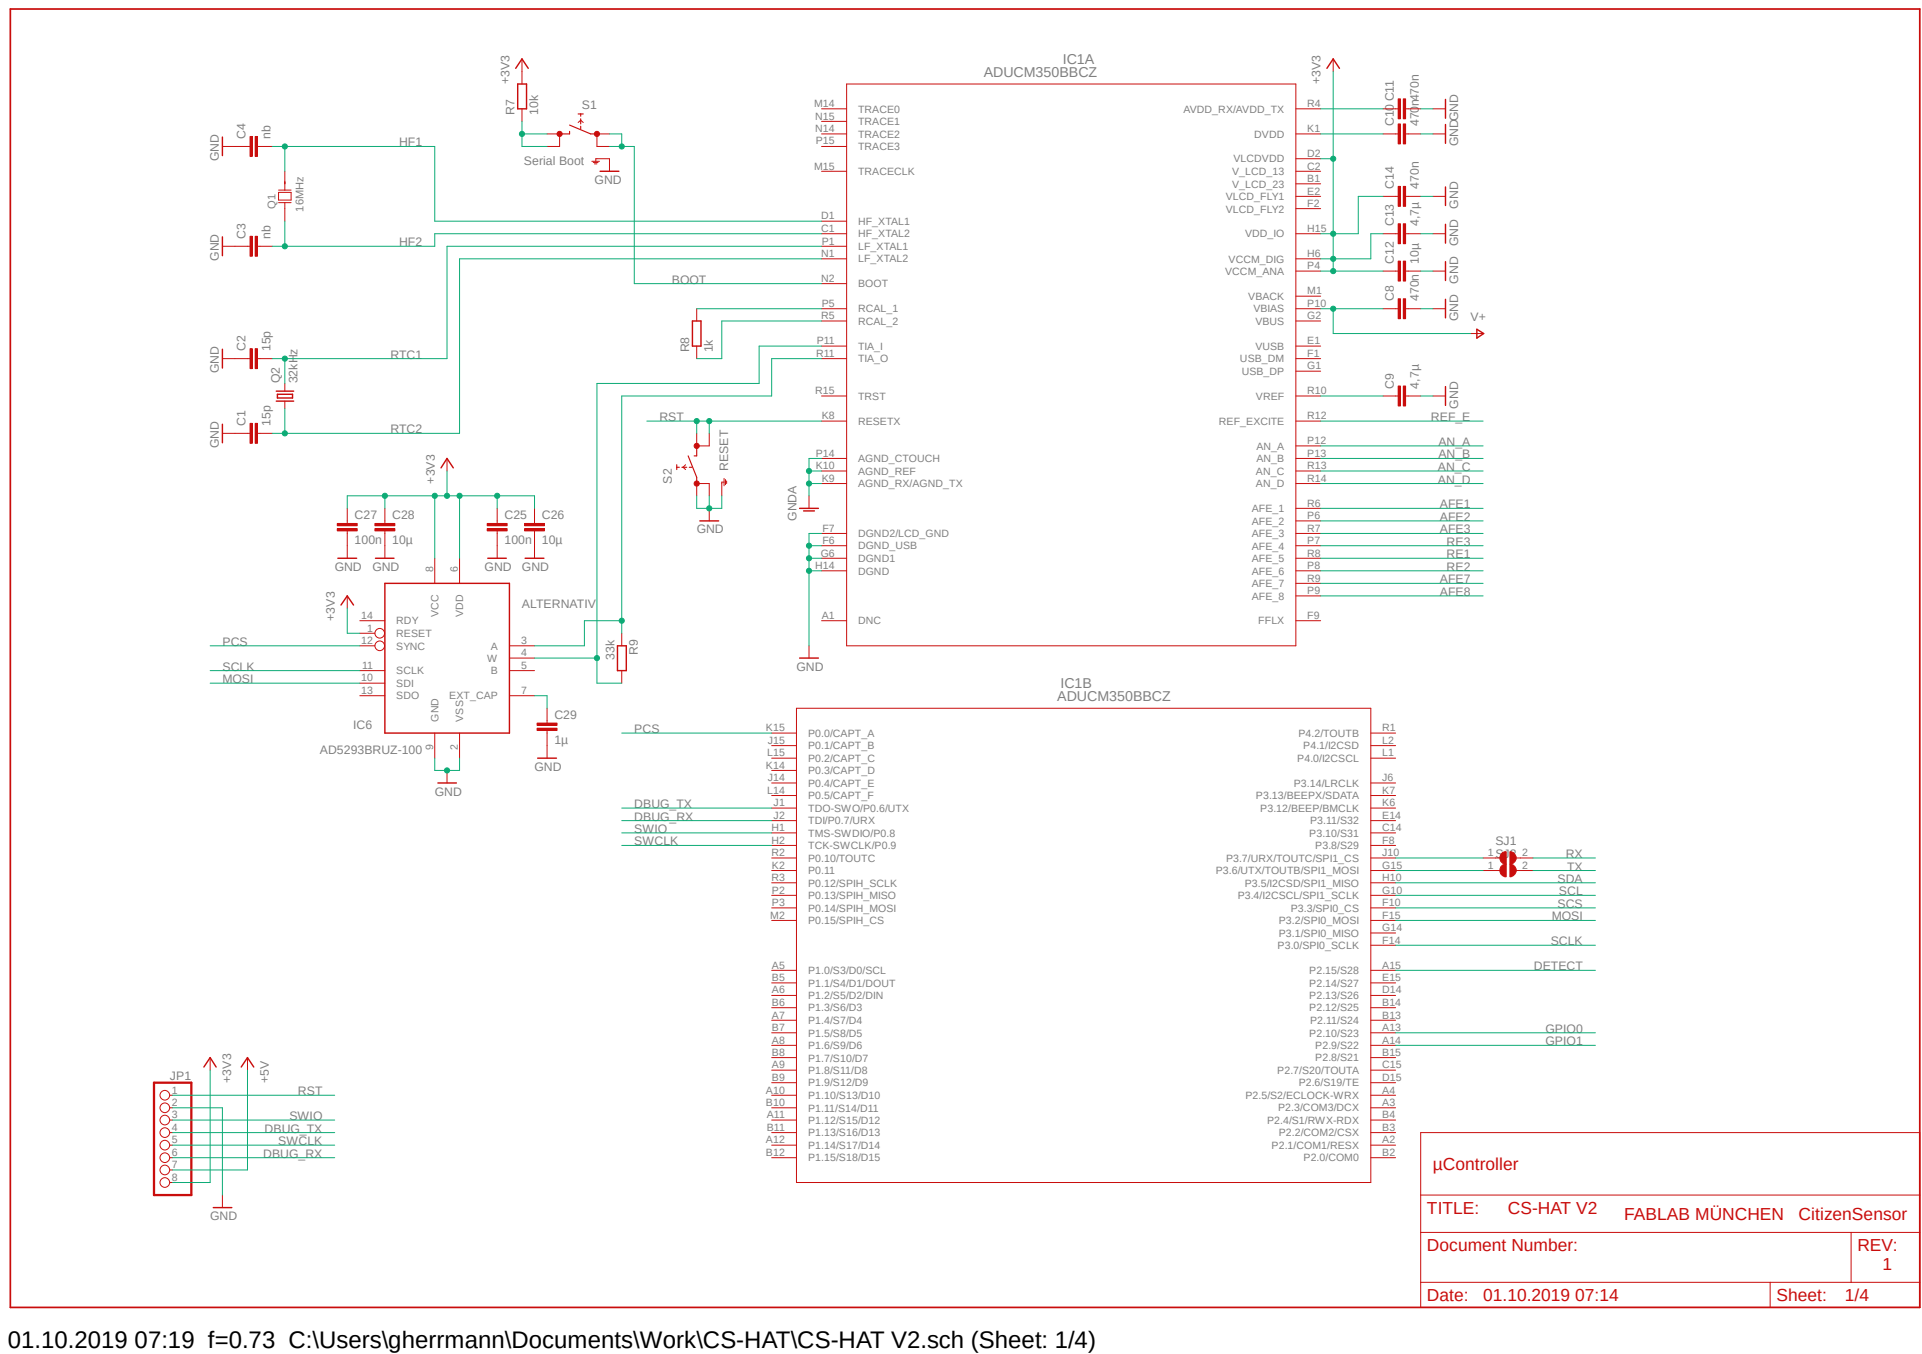
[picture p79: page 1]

GND GND GND GNDGND

GND GND

LF_XTAL1 P1
LF_XTAL2 N1

BOOT | BOOT N2

Document Number: | REV: 1

Date: 01.10.2019 07:14 | Sheet: 1/4

01.10.2019 07:19 f=0.73 C:\Users\gherrmann\Documents\Work\CS-HAT\CS-HAT V2.sch (Sheet: 1/4)

A1 | B1
A2 | B2

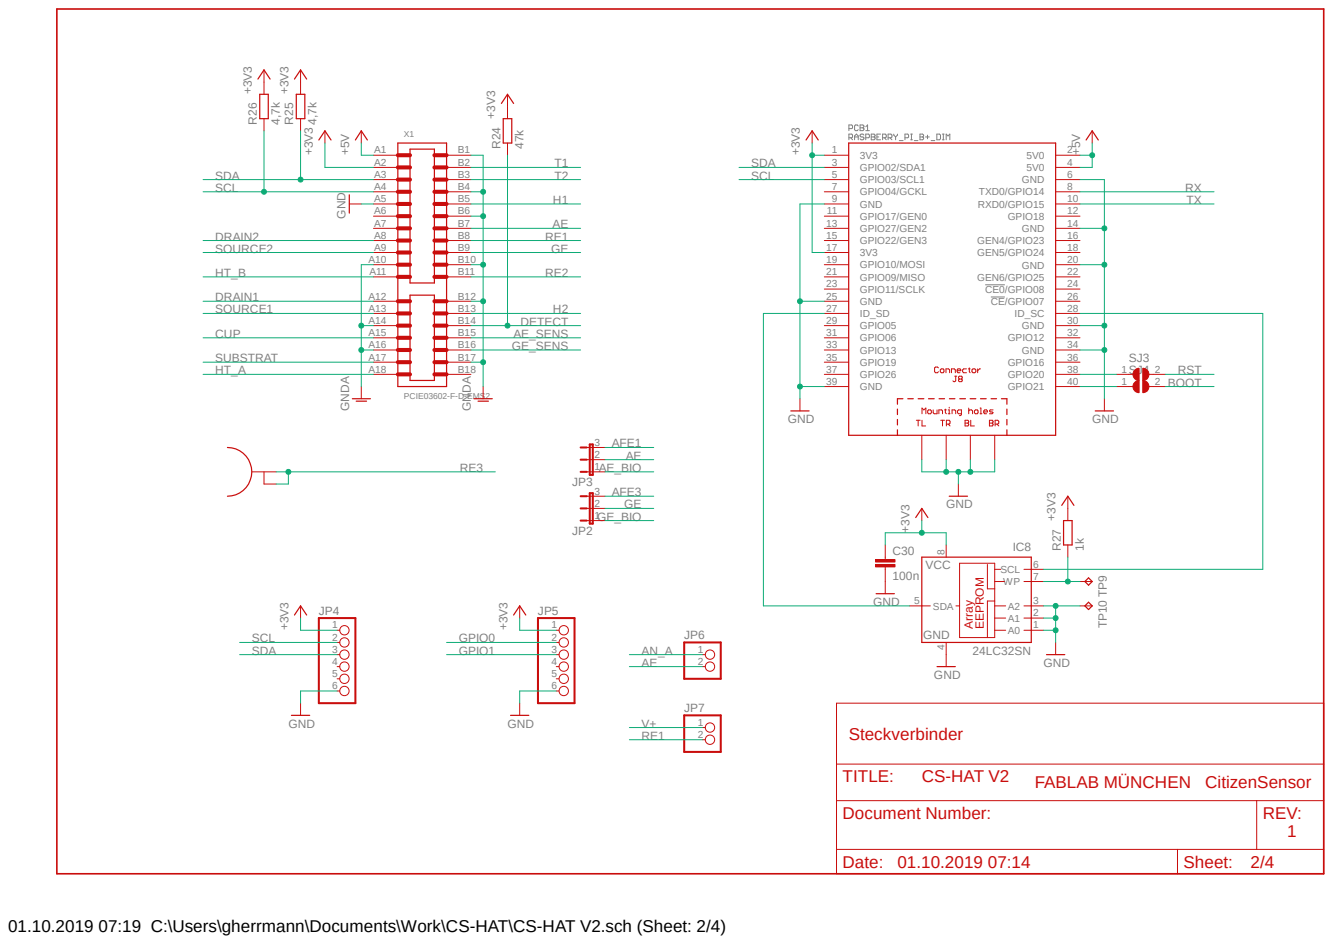
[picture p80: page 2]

Document Number: | REV: 1

01.10.2019 07:19 C:\Users\gherrmann\Documents\Work\CS-HAT\CS-HAT V2.sch (Sheet: 2/4)

4,99k

4,99k

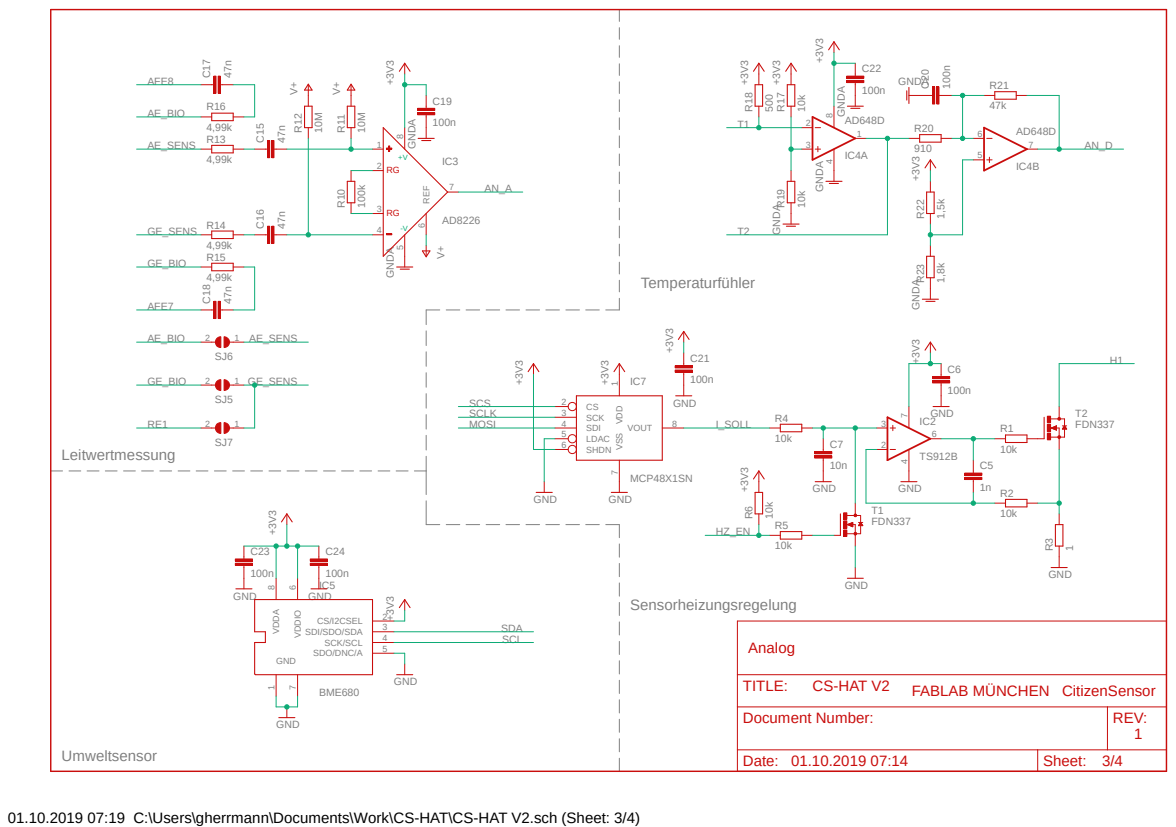
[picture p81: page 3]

Document Number: | REV: 1

01.10.2019 07:19 C:\Users\gherrmann\Documents\Work\CS-HAT\CS-HAT V2.sch (Sheet: 3/4)

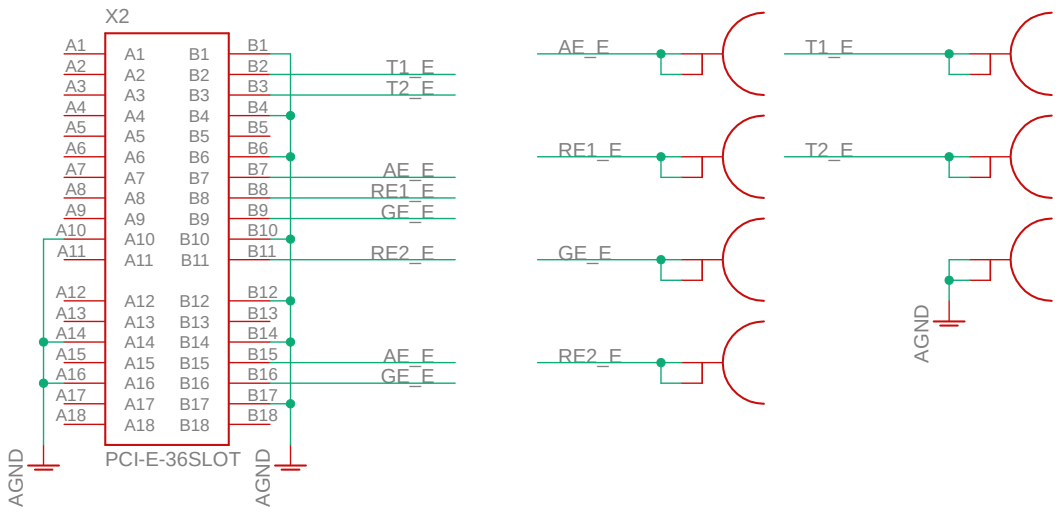
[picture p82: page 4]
PCI-E-36SLOT; AGND; Bananenbuchsen-Adapter; TITLE:; CS-HAT V2

FABLAB MÜNCHEN CitizenSensor

Document Number: | REV: 1

01.10.2019 07:19 C:\Users\gherrmann\Documents\Work\CS-HAT\CS-HAT V2.sch (Sheet: 4/4)

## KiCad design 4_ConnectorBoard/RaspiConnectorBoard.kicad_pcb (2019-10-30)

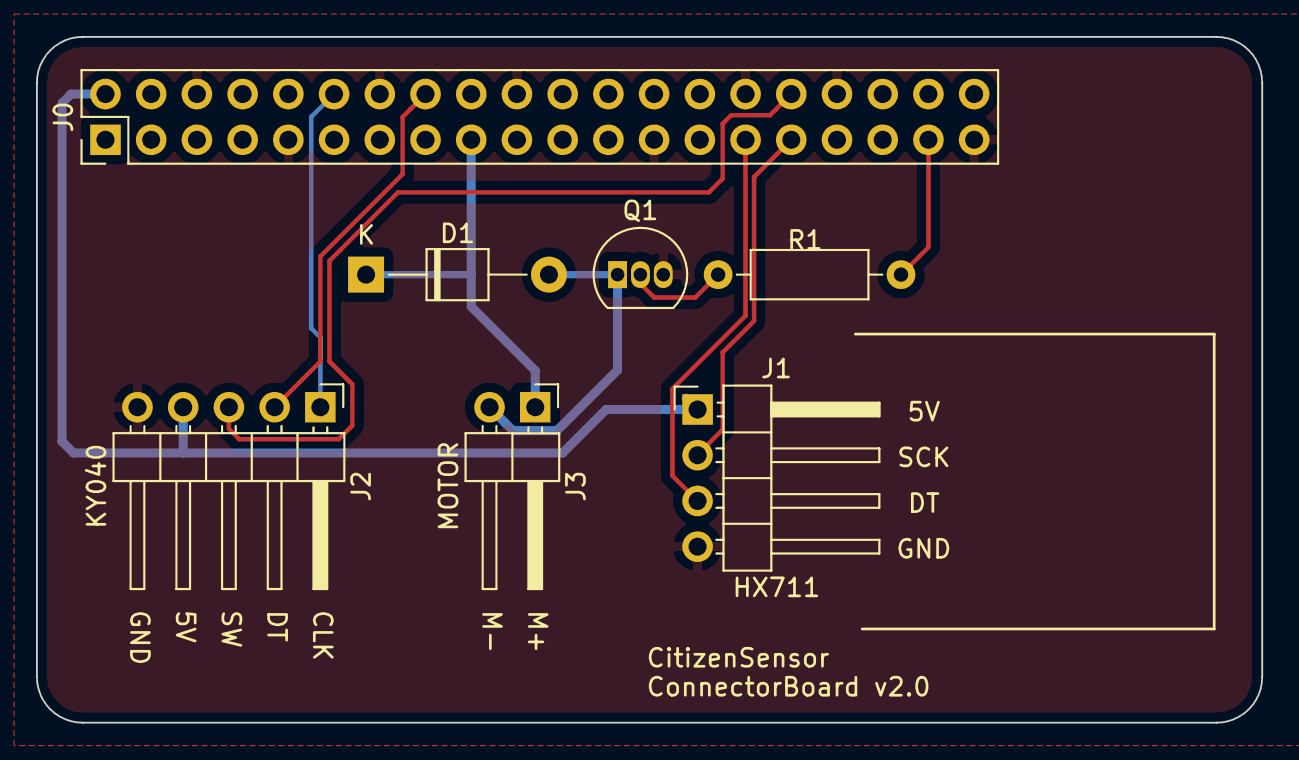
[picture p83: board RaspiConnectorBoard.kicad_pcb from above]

Board: 2 copper layers, 68.1 x 38.1 mm, 7 parts (0 on the bottom side), 11 nets.

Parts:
D1: 1N4004; D_T-1_P10.16mm_Horizontal
J0: Raspberry_Pi_2_3; PinHeader_2x20_P2.54mm_Vertical
J1: HX711; PinHeader_1x04_P2.54mm_Horizontal
J2: KY040; PinHeader_1x05_P2.54mm_Horizontal
J3: MOTOR; PinHeader_1x02_P2.54mm_Horizontal
Q1: BC547; TO-92_Inline
R1: 1K; R_Axial_DIN0207_L6.3mm_D2.5mm_P10.16mm_Horizontal

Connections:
+3V3: D1.1, J0.17, J3.1
+5V: J0.2, J1.1, J2.4
GND: J0.6, J0.9, J0.14, J0.20, J0.25, J0.30, J0.34, J0.39, J1.4, J2.5, Q1.3
HX711_DT: J0.29, J1.3
HX711_SCK: J0.31, J1.2
KY040_CLK: J0.12, J2.1
KY040_DT: J0.16, J2.2
KY040_SW: J0.32, J2.3
MOTOR_PWM: J0.37, R1.2
unnamed: D1.2, J3.2, Q1.1
unnamed: Q1.2, R1.1

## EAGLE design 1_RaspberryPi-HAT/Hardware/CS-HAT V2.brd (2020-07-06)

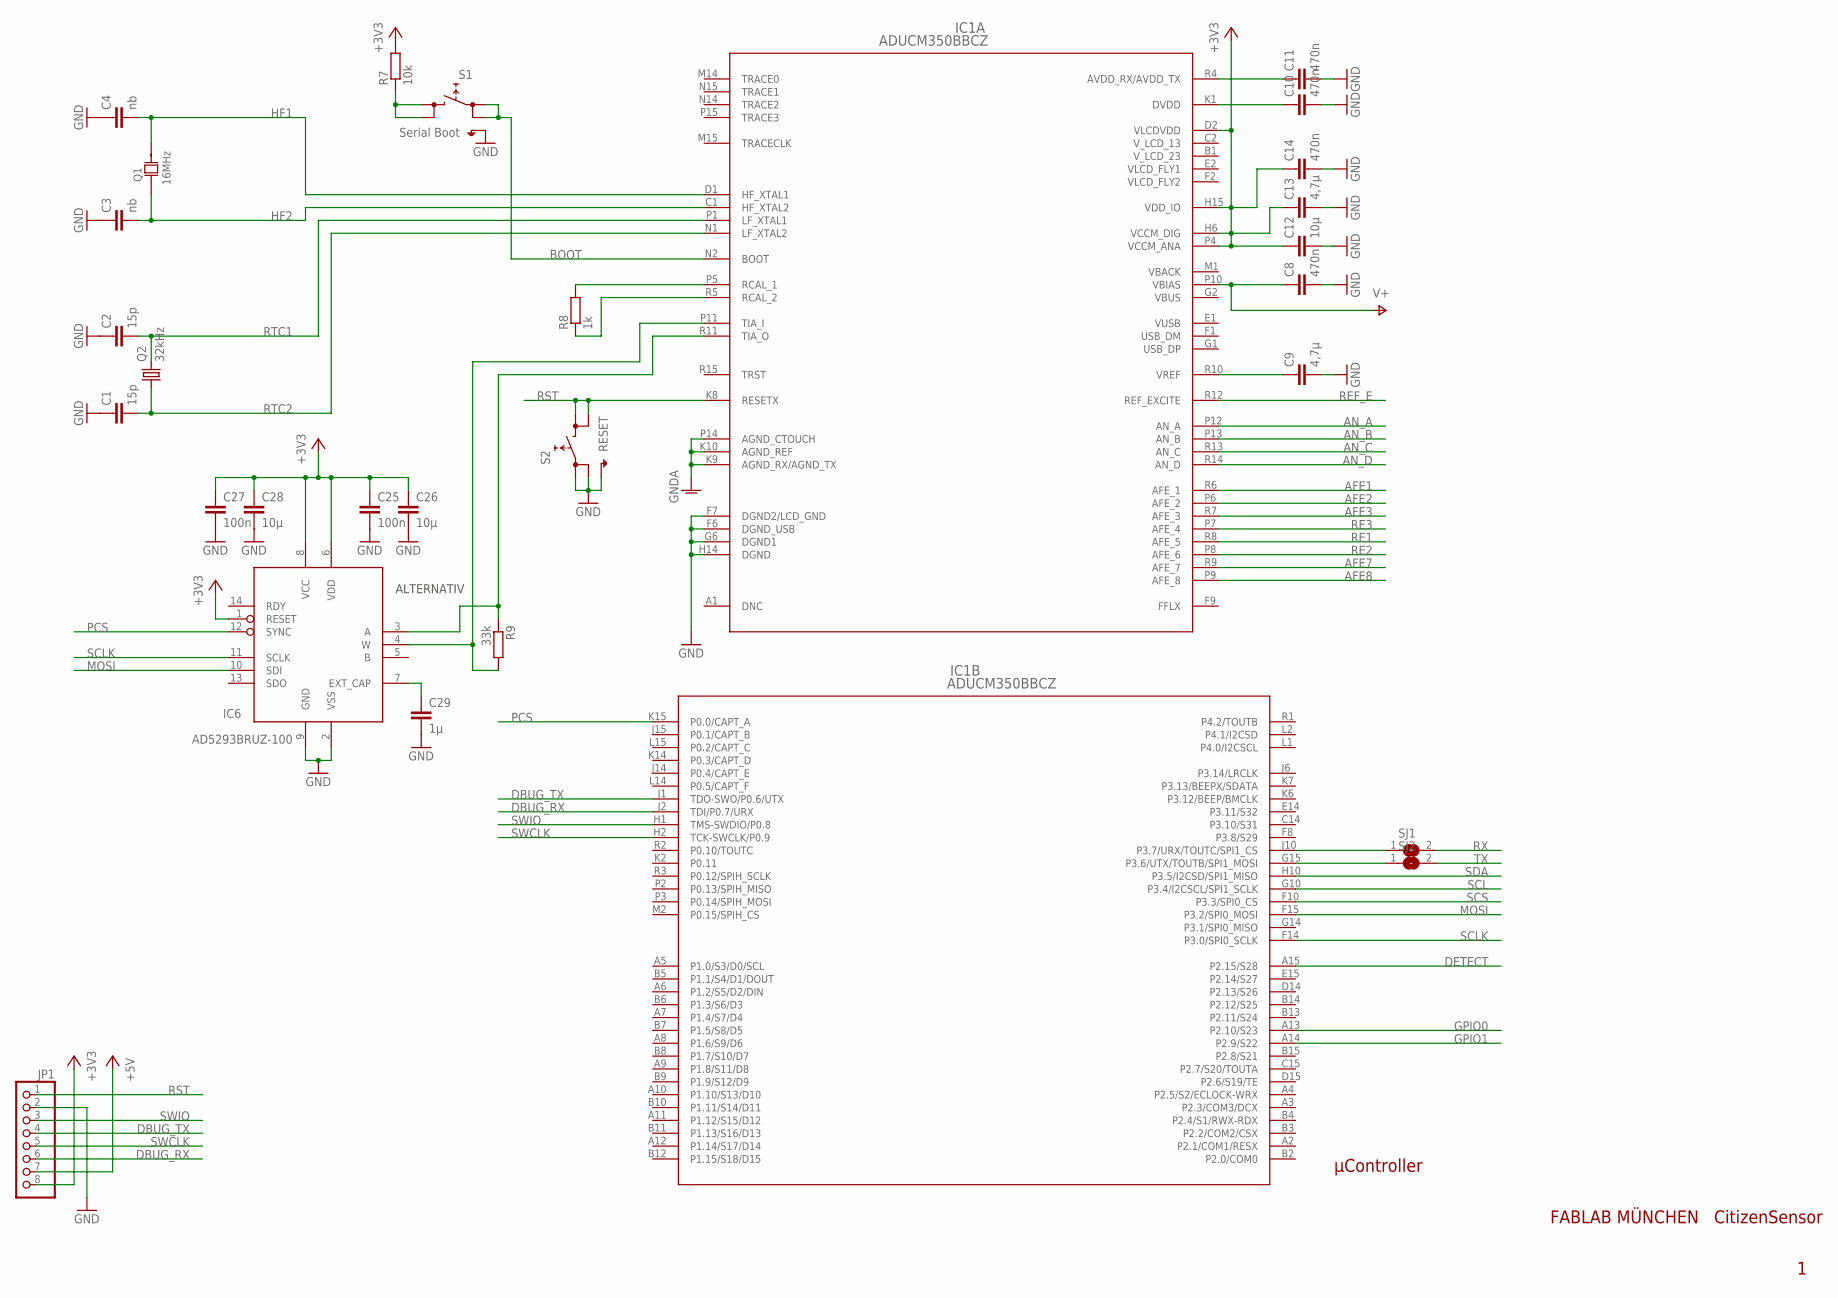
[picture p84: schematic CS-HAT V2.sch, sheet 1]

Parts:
C1, C2: 15p; C0805
C3, C4: nb; C0805
C8, C10, C11, C14: 470n; C0805
C9, C13: 4,7µ; C1206
C12, C26, C28: 10µ; C1206
C25, C27: 100n; C0805
C29: 1µ; C1206
IC1: ADUCM350BBCZ; BC_120_3
IC6: AD5293BRUZ-100; TSSOP14
JP1: PINHD-1X8S; 1X08S
Q1: 16MHz; JXS53
Q2: 32kHz; FC-12M
R7: 10k; R0805
R8: 1k; R0805
R9: 33k; R0805
S1: Serial Boot; SKHMPXE010
S2: RESET; SKHMPXE010
SJ1, SJ2: SJ

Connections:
+3V3: C12.1, C13.1, C14.1, C25.1, C26.1, C27.1, C28.1, IC1.D2 (VLCDVDD), IC1.H6 (VCCM_DIG), IC1.H15 (VDD_IO), IC1.P4 (VCCM_ANA), IC6.1 (RESET), IC6.6 (VDD), IC6.8 (VCC), JP1.8, R7.2; also elsewhere on the board
+5V: JP1.7; also elsewhere on the board
AFE1: IC1.R6 (AFE_1); also elsewhere on the board
AFE2: IC1.P6 (AFE_2)
AFE3: IC1.R7 (AFE_3); also elsewhere on the board
AFE7: IC1.R9 (AFE_7); also elsewhere on the board
AFE8: IC1.P9 (AFE_8); also elsewhere on the board
AN_A: IC1.P12 (AN_A); also elsewhere on the board
AN_B: IC1.P13 (AN_B)
AN_C: IC1.R13 (AN_C)
AN_D: IC1.R14 (AN_D); also elsewhere on the board
BOOT: IC1.N2 (BOOT), S1.1 (1.1), S1.2 (1.2); also elsewhere on the board
DBUG_RX: IC1.J2 (TDI/P0.7/URX), JP1.6
DBUG_TX: IC1.J1 (TDO-SWO/P0.6/UTX), JP1.4
DETECT: IC1.A15 (P2.15/S28); also elsewhere on the board
GND: C1.1, C2.1, C3.1, C4.1, C8.2, C9.2, C10.2, C11.2, C12.2, C13.2, C14.2, C25.2, C26.2, C27.2, C28.2, C29.2, IC1.F6 (DGND_USB), IC1.F7 (DGND2/LCD_GND), IC1.G6 (DGND1), IC1.H14 (DGND), IC6.2 (VSS), IC6.9 (GND), JP1.2, S1.5 (SH), S2.1 (1.1), S2.2 (1.2), S2.5 (SH); also elsewhere on the board
GNDA: IC1.K9 (AGND_RX/AGND_TX), IC1.K10 (AGND_REF), IC1.P14 (AGND_CTOUCH); also elsewhere on the board
GPIO0: IC1.A13 (P2.10/S23); also elsewhere on the board
GPIO1: IC1.A14 (P2.9/S22); also elsewhere on the board
HF1: C4.2, IC1.D1 (HF_XTAL1), Q1.3 (2)
HF2: C3.2, IC1.C1 (HF_XTAL2), Q1.1
MOSI: IC1.F15 (P3.2/SPI0_MOSI), IC6.10 (SDI); also elsewhere on the board
unnamed: IC1.J10 (P3.7/URX/TOUTC/SPI1_CS), SJ1.1
unnamed: IC1.G15 (P3.6/UTX/TOUTB/SPI1_MOSI), SJ2.1
unnamed: R7.1, S1.3 (2.1), S1.4 (2.2)
unnamed: C29.1, IC6.7 (EXT_CAP)
unnamed: IC1.P5 (RCAL_1), R8.2
unnamed: IC1.R5 (RCAL_2), R8.1
unnamed: IC1.P11 (TIA_I), IC6.4 (W), R9.2
unnamed: IC1.R11 (TIA_O), IC6.3 (A), R9.1
unnamed: C9.1, IC1.R10 (VREF)
unnamed: C10.1, IC1.K1 (DVDD)
unnamed: C11.1, IC1.R4 (AVDD_RX/AVDD_TX)
PCS: IC1.K15 (P0.0/CAPT_A), IC6.12 (SYNC)
RE1: IC1.R8 (AFE_5); also elsewhere on the board
RE2: IC1.P8 (AFE_6); also elsewhere on the board
RE3: IC1.P7 (AFE_4); also elsewhere on the board
REF_E: IC1.R12 (REF_EXCITE)
RST: IC1.K8 (RESETX), JP1.1, S2.3 (2.1), S2.4 (2.2); also elsewhere on the board
RTC1: C2.2, IC1.P1 (LF_XTAL1), Q2.2
RTC2: C1.2, IC1.N1 (LF_XTAL2), Q2.1
RX: SJ1.2; also elsewhere on the board
SCL: IC1.G10 (P3.4/I2CSCL/SPI1_SCLK); also elsewhere on the board
SCLK: IC1.F14 (P3.0/SPI0_SCLK), IC6.11 (SCLK); also elsewhere on the board
SCS: IC1.F10 (P3.3/SPI0_CS); also elsewhere on the board
SDA: IC1.H10 (P3.5/I2CSD/SPI1_MISO); also elsewhere on the board
SWCLK: IC1.H2 (TCK-SWCLK/P0.9), JP1.5
SWIO: IC1.H1 (TMS-SWDIO/P0.8), JP1.3
TX: SJ2.2; also elsewhere on the board
V+: C8.1, IC1.P10 (VBIAS); also elsewhere on the board

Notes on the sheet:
FABLAB MÜNCHEN CitizenSensor
µController
ALTERNATIV

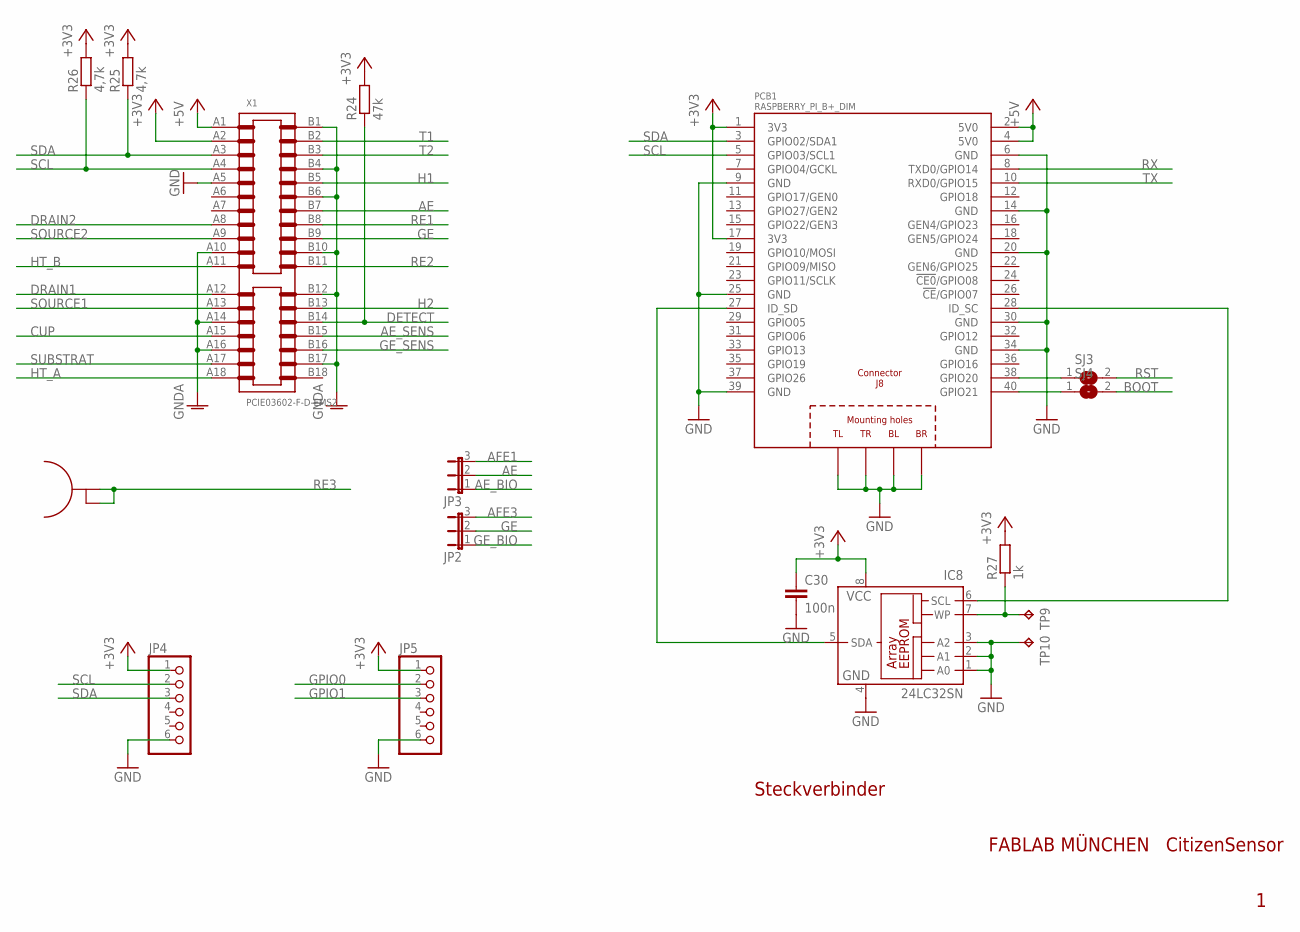
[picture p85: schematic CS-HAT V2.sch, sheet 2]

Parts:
C30: 100n; C0805
IC8: 24LC32SN; SO-08
JP2, JP3: JP2ES; JP2S
JP4, JP5: PINHD-1X6S; 1X06S
PCB1: RASPBERRY_PI_B+_DIM; RASPBERRY_PI_BPLUS_DIM
R24: 47k; R0805
R25, R26: 4,7k; R0805
R27: 1k; R0805
SJ3, SJ4: SJ
TP8: TESTPLUG2MM
TP9, TP10: TPB2,54; B2,54
X1: PCIE03602-F-D-EMS2; PCIE-036-02-F-D-EMS2

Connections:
+3V3: C30.1, IC8.8 (VCC), JP4.1, JP5.1, PCB1.1 (3V3), PCB1.17 (3V3), R24.2, R25.2, R26.2, R27.2, X1.A2; also elsewhere on the board
+5V: PCB1.2 (5V0), PCB1.4 (5V0), X1.A1; also elsewhere on the board
AE: JP3.2, X1.B7
AE_BIO: JP3.1; also elsewhere on the board
AE_SENS: X1.B15; also elsewhere on the board
AFE1: JP3.3; also elsewhere on the board
AFE3: JP2.3; also elsewhere on the board
BOOT: SJ4.2; also elsewhere on the board
CUP: X1.A15
DETECT: R24.1, X1.B14; also elsewhere on the board
DRAIN1: X1.A12
DRAIN2: X1.A8
GE: JP2.2, X1.B9
GE_BIO: JP2.1; also elsewhere on the board
GE_SENS: X1.B16; also elsewhere on the board
GND: C30.2, IC8.1 (A0), IC8.2 (A1), IC8.3 (A2), IC8.4 (GND), JP4.6, JP5.6, PCB1.6 (GND), PCB1.9 (GND), PCB1.14 (GND), PCB1.20 (GND), PCB1.25 (GND), PCB1.30 (GND), PCB1.34 (GND), PCB1.39 (GND), PCB1.PE_BL (BL), PCB1.PE_BR (BR), PCB1.PE_TL (TL), PCB1.PE_TR (TR), TP10.TP, X1.A5; also elsewhere on the board
GNDA: X1.A10, X1.A14, X1.A16, X1.B1, X1.B4, X1.B6, X1.B10, X1.B12, X1.B17; also elsewhere on the board
GPIO0: JP5.2; also elsewhere on the board
GPIO1: JP5.3; also elsewhere on the board
H1: X1.B5; also elsewhere on the board
H2: X1.B13
HT_A: X1.A18
HT_B: X1.A11
unnamed: PCB1.40 (GPIO21), SJ4.1
unnamed: PCB1.38 (GPIO20), SJ3.1
unnamed: IC8.5 (SDA), PCB1.27 (ID_SD)
unnamed: IC8.6 (SCL), PCB1.28 (ID_SC)
unnamed: IC8.7 (WP), R27.1, TP9.TP
RE1: X1.B8; also elsewhere on the board
RE2: X1.B11; also elsewhere on the board
RE3: TP8.A, TP8.B; also elsewhere on the board
RST: SJ3.2; also elsewhere on the board
RX: PCB1.8 (TXD0/GPIO14); also elsewhere on the board
SCL: JP4.2, PCB1.5 (GPIO03/SCL1), R26.1, X1.A4; also elsewhere on the board
SDA: JP4.3, PCB1.3 (GPIO02/SDA1), R25.1, X1.A3; also elsewhere on the board
SOURCE1: X1.A13
SOURCE2: X1.A9
SUBSTRAT: X1.A17
T1: X1.B2; also elsewhere on the board
T2: X1.B3; also elsewhere on the board
TX: PCB1.10 (RXD0/GPIO15); also elsewhere on the board

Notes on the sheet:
FABLAB MÜNCHEN CitizenSensor
Steckverbinder

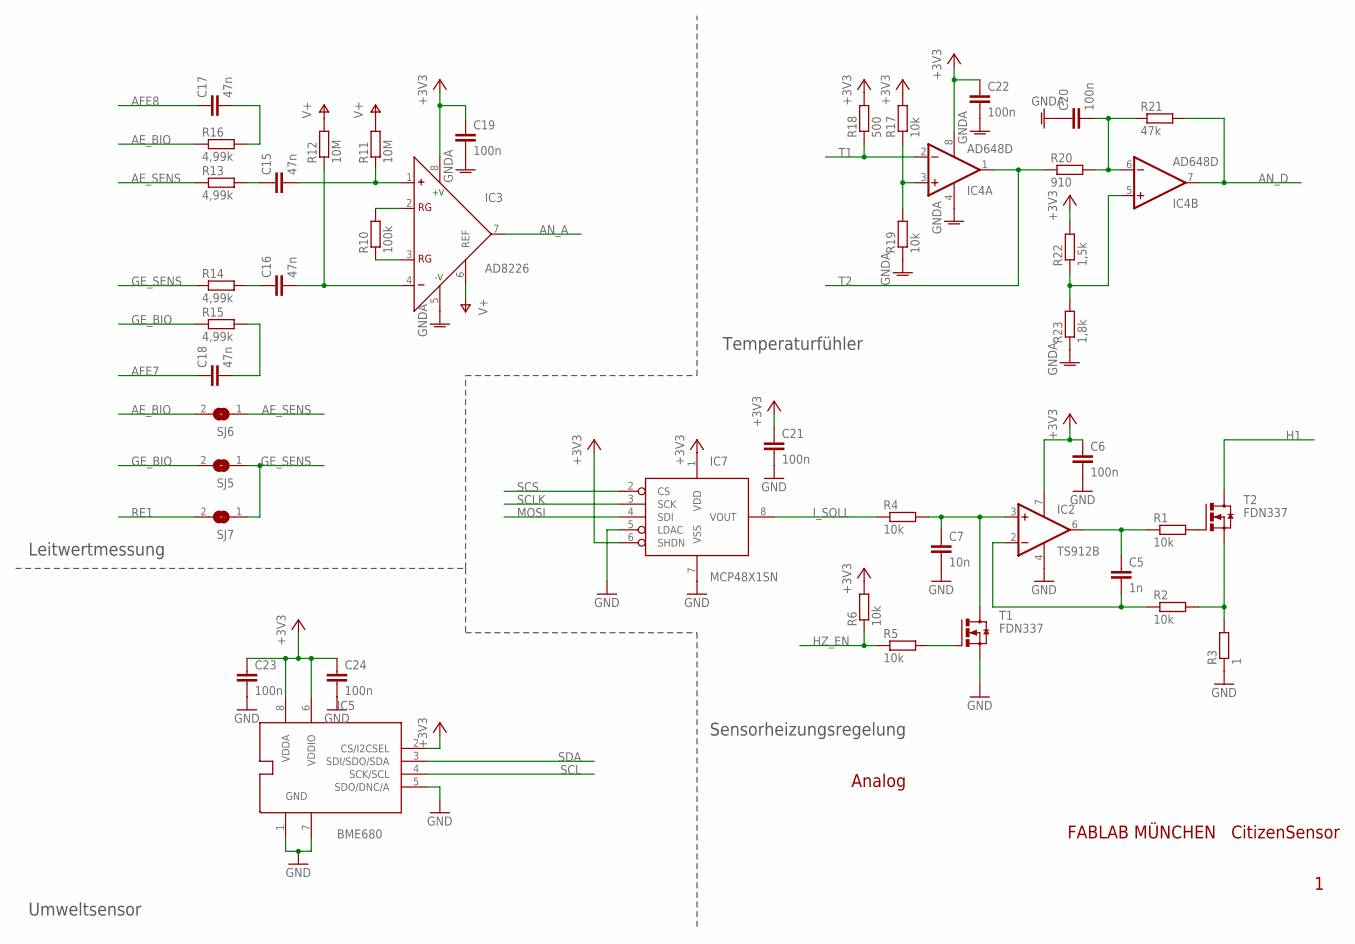
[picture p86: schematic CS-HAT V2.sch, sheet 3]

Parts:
C5: 1n; C0805
C6, C19, C20, C21, C22, C23, C24: 100n; C0805
C7: 10n; C0805
C15, C16, C17, C18: 47n; C0805
IC2: TS912B; SO08
IC3: AD8226; SO8
IC4: AD648D; SO08
IC5: BME680
IC7: MCP48X1SN; SO-08
R1, R2, R4, R5, R6, R17, R19: 10k; R0805
R3: 1; R1210
R10: 100k; R0805
R11, R12: 10M; R0805
R13, R14, R15, R16: 4,99k; R0805
R18: 500; R0805
R20: 910; R0805
R21: 47k; R0805
R22: 1,5k; R0805
R23: 1,8k; R0805
SJ5, SJ6, SJ7: SJ
T1, T2: FDN337; SUPER-SOT3

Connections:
+3V3: C6.1, C19.1, C21.1, C22.1, C23.1, C24.1, IC2.7 (V+), IC3.8 (+V), IC4.8 (V+), IC5.2 (CS/I2CSEL), IC5.6 (VDDIO), IC5.8 (VDDA), IC7.1 (VDD), IC7.6 (SHDN), R6.2, R17.2, R18.2, R22.2; also elsewhere on the board
AE_BIO: R16.1, SJ6.2; also elsewhere on the board
AE_SENS: R13.1, SJ6.1; also elsewhere on the board
AFE7: C18.1; also elsewhere on the board
AFE8: C17.1; also elsewhere on the board
AN_A: IC3.7 (OUT); also elsewhere on the board
AN_D: IC4.7 (OUT), R21.2; also elsewhere on the board
GE_BIO: R15.1, SJ5.2; also elsewhere on the board
GE_SENS: R14.1, SJ5.1, SJ7.1; also elsewhere on the board
GND: C6.2, C7.2, C21.2, C23.2, C24.2, IC2.4 (V-), IC5.1 (GND), IC5.5 (SDO/DNC/A), IC5.7 (GND), IC7.5 (LDAC), IC7.7 (VSS), R3.1, T1.2 (S); also elsewhere on the board
GNDA: C19.2, C20.1, C22.2, IC3.5 (-V), IC4.4 (V-), R19.1, R23.1; also elsewhere on the board
H1: T2.3 (D); also elsewhere on the board
HZ_EN: R5.1, R6.1
I_SOLL: IC7.8 (VOUT), R4.1
MOSI: IC7.4 (SDI); also elsewhere on the board
unnamed: C5.1, IC2.6 (OUT), R1.1
unnamed: C5.2, IC2.2 (-IN), R2.1
unnamed: R1.2, T2.1 (G)
unnamed: R2.2, R3.2, T2.2 (S)
unnamed: C7.1, IC2.3 (+IN), R4.2, T1.3 (D)
unnamed: R5.2, T1.1 (G)
unnamed: IC3.2 (RG), R10.2
unnamed: C18.2, R15.2
unnamed: IC3.3 (RG), R10.1
unnamed: C15.2, IC3.1 (+), R11.1
unnamed: C16.2, IC3.4 (-), R12.1
unnamed: C16.1, R14.2
unnamed: C15.1, R13.2
unnamed: C17.2, R16.2
unnamed: IC4.3 (+IN), R17.1, R19.2
unnamed: C20.2, IC4.6 (-IN), R20.2, R21.1
unnamed: IC4.5 (+IN), R22.1, R23.2
RE1: SJ7.2; also elsewhere on the board
SCL: IC5.4 (SCK/SCL); also elsewhere on the board
SCLK: IC7.3 (SCK); also elsewhere on the board
SCS: IC7.2 (CS); also elsewhere on the board
SDA: IC5.3 (SDI/SDO/SDA); also elsewhere on the board
T1: IC4.2 (-IN), R18.1; also elsewhere on the board
T2: IC4.1 (OUT), R20.1; also elsewhere on the board
V+: IC3.6 (REF), R11.2, R12.2; also elsewhere on the board

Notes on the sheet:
FABLAB MÜNCHEN CitizenSensor
Analog
Leitwertmessung
Umweltsensor
Sensorheizungsregelung
Temperaturfühler

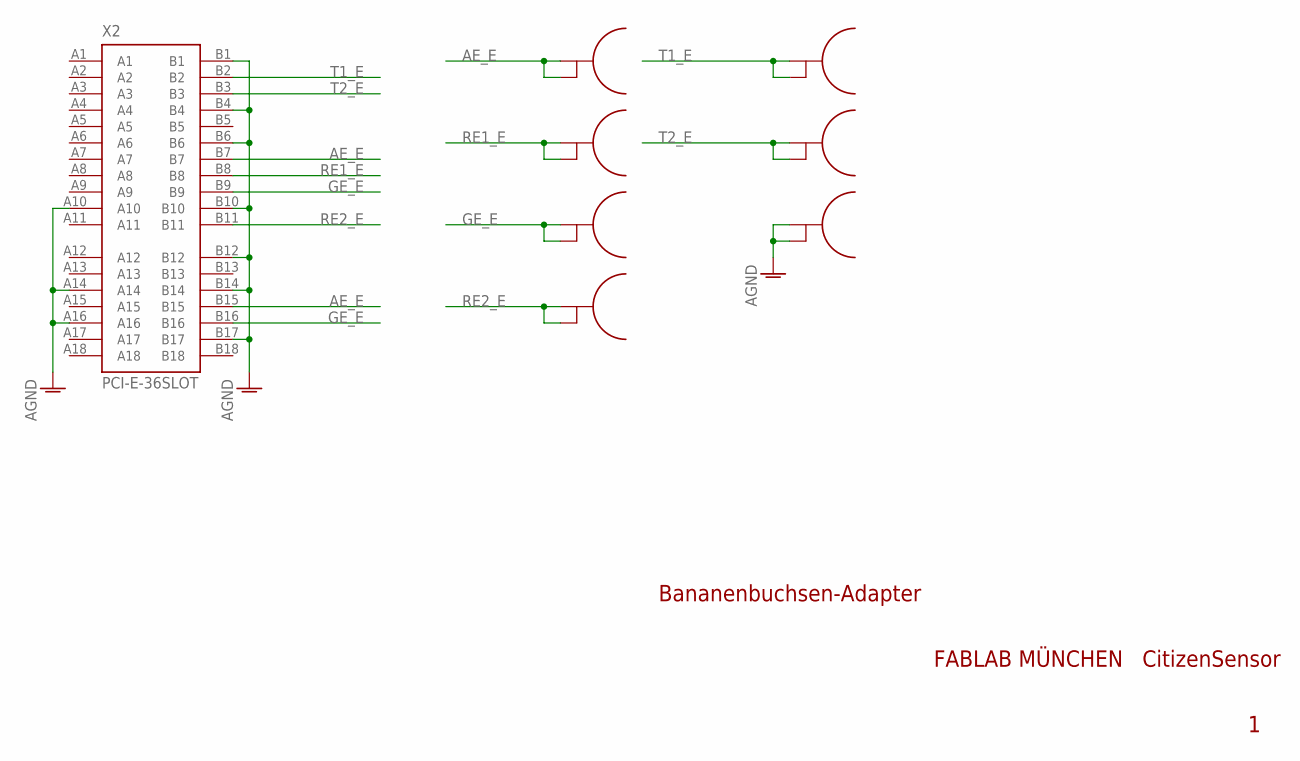
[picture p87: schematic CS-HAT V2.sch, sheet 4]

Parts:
TP1, TP2, TP3, TP4, TP5, TP6, TP7: TESTPLUG2MM
X2: PCI-E-36SLOT; PCI-E-36_SLOT

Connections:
AE_E: TP1.A, TP1.B, X2.B7, X2.B15
AGND: TP7.A, TP7.B, X2.A10, X2.A14, X2.A16, X2.B1, X2.B4, X2.B6, X2.B10, X2.B12, X2.B14, X2.B17
GE_E: TP3.A, TP3.B, X2.B9, X2.B16
RE1_E: TP2.A, TP2.B, X2.B8
RE2_E: TP4.A, TP4.B, X2.B11
T1_E: TP5.A, TP5.B, X2.B2
T2_E: TP6.A, TP6.B, X2.B3

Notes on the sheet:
FABLAB MÜNCHEN CitizenSensor
Bananenbuchsen-Adapter

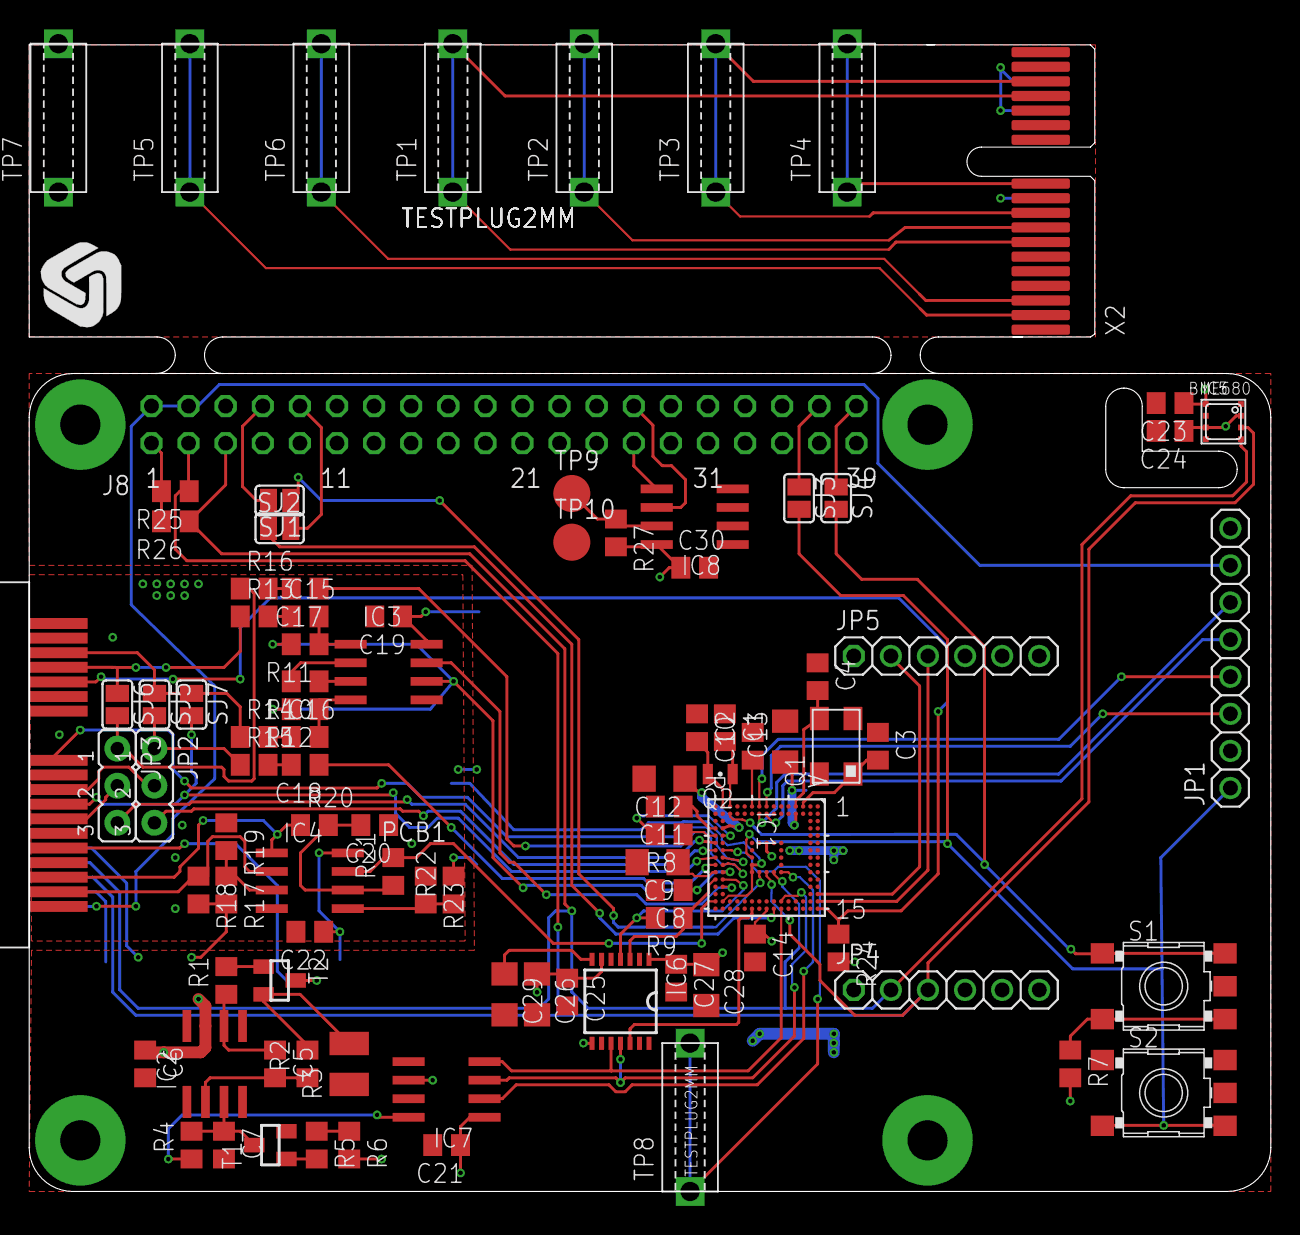
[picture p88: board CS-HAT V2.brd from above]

Board: 2 copper layers, 85.0 x 56.0 mm, 96 parts (0 on the bottom side), 86 nets.

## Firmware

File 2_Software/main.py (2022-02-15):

#!/usr/bin/env python3
# -*- coding: utf-8 -*-
"""
Created on Thu Jul 19 15:05:15 2018

@author: soussi, steinmassl, stahl @ Fraunhofer EMFT; hottarek @ Fablab München

License Information:
hx711: Copyright 2019 https://github.com/tatobari
KY040: Copyright (c) 2017 Martin O'Hanlon https://github.com/martinohanlon
mysql.connector: Copyright © 2012, 2020, Oracle and/or its affiliates. All rights reserved.
netifaces: Copyright (c) 2007-2018 Alastair Houghton https://github.com/al45tair
serial: Copyright David Belais
GPIO: Copyright (c) 2012-2014 Ben Croston
numpy: Copyright © 2005-2020, NumPy Developers
pandas: Copyright (c) 2008-2012, AQR Capital Management, LLC, Lambda Foundry, Inc. and PyData Development Team All rights reserved.
"""

'''
Grid for TKinter Window:
      0         1          2         3
  -----------------------------------------
0 ¦    step_name     ¦                    ¦
--¦------------------¦                    ¦
1 ¦ precaution_short ¦       Image        ¦
--¦------------------¦                    ¦
2 ¦                  ¦                    ¦
--¦   precautions_   ¦                    ¦
3 ¦       long       ¦                    ¦
--¦------------------¦                    ¦
4 ¦bt_back ¦ bt_next ¦                    ¦
--¦------------------¦--------------------¦
5 ¦       space for logos      ¦    Step_#¦
  -----------------------------------------
'''
import sys
import os
import mysql.connector as mariadb
# for IP Adress ETH0
import netifaces

#Create relative paths:
fileDir = os.path.dirname(os.path.abspath(__file__))

if os.name == 'nt': #windows
    from matplotlib.backends.backend_tkagg import FigureCanvasTkAgg, NavigationToolbar2Tk#Agg
if os.name == 'posix': #linux
    #on raspbian, matplotlib was installed using apt-get install python3-matplotlib
    #this uses the deprecated NavigationToolbar2TkAgg
    #handle different runtime-environments...
    try:
        from matplotlib.backends.backend_tkagg import FigureCanvasTkAgg, NavigationToolbar2Tk#Agg
    except:
        from matplotlib.backends.backend_tkagg import FigureCanvasTkAgg, NavigationToolbar2TkAgg

from matplotlib.backend_bases import *
from matplotlib.figure import Figure
import usb.core #install libusb.dll and pyusb to be able to use this

import serial
import serial.tools.list_ports

if os.name == 'posix':
    #rotary encoder:
    import RPi.GPIO as GPIO
    from ky040.KY040 import KY040
    #load cell electronics
    from hx711 import HX711

from tkinter import *
import tkinter as tk
from tkinter.font import Font
import tkinter.messagebox as ms
from tkinter.ttk import  Frame
import pandas as pd
import numpy as np
import subprocess

from PIL import Image # in order to resize

from time import sleep #time is distributed with python

#global variables
step_next_index=0 #do not change
scale_factor = 0.9 #how much vertical space the image should cover
fullscreen_mode = 1
current_step=0 #makes current step accessable from outside step
bgwindow_global=0
entry_confirmed=False
choosen_concentration=0
real_concentration=0
main_menu_entry=-2 # Start with Splash-Screen ... -1 would be mainmenu
main_exit=False
# For creating calibration solutions
last_scale_val=0
mSaltUser=0
mStockUser=0

last_ADu_val = 0

if os.name == 'posix':
    #KY 040 rotary Encoder
    CLOCKPIN = 18 #CS-ConnectorBoard V1.0
    DATAPIN = 23 #CS-ConnectorBoard V1.0
    SWITCHPIN = 12 #CS-ConnectorBoard V1.0
    #HX711 load cell encoder
    SCKPIN = 6
    DTPIN = 5
    REFERENCE_UNIT = 1.94 # 1kg-Element (HOTTI)
    REFERENCE_UNIT = 12.2 # 100g-Element (Demonstrator)
    #MOTOR
    MOTORPIN = 26
    MOTORFREQ = 1000
    MOTORSTART = 40
    MOTORSET = 25
#class to create the steps and give their fuctionalities

class step:


    def __init__(self,Id,title):

        #making some variables global so that they can be used outside of step class.
        global Id_global,t,end_point_detection_estimated_time_global, current_step, entry_confirmed, bgwindow_global, main_menu_entry, last_scale_val, last_ADu_val, mSaltUser, mStockUser, nCalSol, arrConcCal, arrVolStock, arrVolWater, choice_val, step_next_index

        current_step=self
        self.clicked=0
        self.title=title
        self.Id=Id
        Id_global=self.Id
        #the Excel data sheet is read in the prog in the self.df variable
        self.df = pd.read_csv(r'%s' %os.path.join(fileDir,'steps.csv'), sep=';')
        self.c=self.df.columns
        #self.l is the array containig all Ids of the steps in data base
        self.l=self.df.ID.values

        for self.i in range (1,len(self.l)):

            if float(self.l[self.i]) == self.Id:
                #the parameters of the steps are read from data base in variables, i is the index of each Id in the self.l array.
                self.process_step=self.df['Process step'][self.i]
                self.group=self.df['Unnamed: 2'][self.i]
                self.user_action_required_yn=self.df['User Action Required'][self.i]
                self.user_action_required_description=self.df['Unnamed: 4'][self.i]
                self.changing_process_parameter_name=self.df['Changing process parameter'][self.i]
                self.changing_process_parameter_measurement_method=self.df['Unnamed: 6'][self.i]
                self.end_point_detection_yn=self.df['End-point detection'][self.i]
                self.end_point_detection_decription=self.df['Unnamed: 8'][self.i]
                self.end_point_detection_estimated_time=int(self.df['Unnamed: 9'][self.i])
                self.precautions_Conditions_short=self.df['Precautions/Conditions'][self.i]
                self.precautions_Conditions_long=self.df['Unnamed: 11'][self.i]
                self.imagetext=self.df['Image'][self.i]
                try:
                    self.image=os.path.join(os.path.join(fileDir, 'photos'), self.imagetext)
                except TypeError:
                    self.image=os.path.join(os.path.join(fileDir, 'photos'), 'standard.gif') #one could insert standard image here
                    pass
                #debug:
#                print(self.process_step)


        #end_point_detection_estimated_time_global=self.end_point_detection_estimated_time
        self.input=0
        self.cpos=0
        self.user_entry=""
        self.r=12
        self.tare_pressed = False
        self.target_weight = 0
        #create the tkinter window
        self.window= tk.Toplevel()
        self.tkvar = StringVar(self.window)
        self.scale_var = StringVar()
        self.choice_var = StringVar()
        self.ADu_var = StringVar()
        self.var = StringVar()

        if fullscreen_mode == 1:
            self.window.attributes('-fullscreen', True)
        self.window.attributes("-topmost", True)
        #get resolution
        self.w = int(self.window.winfo_screenwidth())
        self.h = int(self.window.winfo_screenheight())
        self.frame = Frame(self.window)
        self.frame.grid()
        self.window.event_generate('<Motion>', warp=True, x=self.window.winfo_screenwidth(), y=self.window.winfo_screenheight())
        self.window.config(cursor="none")
        #the title is given freely by the user and is displayed on the rand of the window, for example "step1"
        self.window.title(self.title)
        #window_global=self.window
        #defining font of the process_step displayed on the winodw
        if self.h > 1000:
            self.fontTextShort=Font(size=20)
            self.fontTextLong=Font(size=15,slant="italic")
            self.fontStepName=Font(size=20,slant="italic")
            self.fontFooter=Font(size=15)
            self.fontMenuCap=Font(size=30)
            self.fontMenuItem=Font(size=20)
        elif self.h < 1000 and self.h > 450:
            self.fontTextShort=Font(size=11)
            self.fontTextLong=Font(size=10,slant="italic")
            self.fontStepName=Font(size=11,slant="italic")
            self.fontFooter=Font(size=10)
            self.fontMenuCap=Font(size=20)
            self.fontMenuItem=Font(size=15)
        else:
            self.fontTextShort=Font(size=11)
            self.fontTextLong=Font(size=11,slant="italic")
            self.fontStepName=Font(size=9,slant="italic")
            self.fontFooter=Font(size=8)
            self.fontMenuCap=Font(size=30)
            self.fontMenuItem=Font(size=20)

        if self.Id not in [401,402,301,5001,598,599,7001]: # [Hauptmenü, Netzwerk-Info, Reset-choice]
            tk.Label(self.window, text=name + ': ' + self.process_step, font=self.fontStepName,wraplength=(self.w-scale_factor*self.h)).grid(column=0,row=0,columnspan=2,sticky=W) # writing process step on window
            tk.Label(self.window, text=self.precautions_Conditions_short,font=self.fontTextShort,wraplength=(self.w-scale_factor*self.h)).grid(row=1,column=0,columnspan=2,sticky=W) #text=self.user_action_required_description,font=self.fontTextLong,bg="white",width=60).grid(row=90,column=30,sticky='E')#writing user action on window
            tk.Label(self.window, text=self.precautions_Conditions_long,font=self.fontTextLong,wraplength=(self.w-scale_factor*self.h)).grid(row=3,column=0,columnspan=2,rowspan=2,sticky=W)
            tk.Label(self.window, text=('Schritt '+str(step_next_index+1)+' von '+str(num_steps)+'      '),font=self.fontFooter).grid(row=5,column=2,columnspan=2,sticky=SE)
            #self.Button1=tk.Button(self.window,text=">>",font=self.fontTextLong,command=self.execute).grid(row=4,column=1) #next
            #self.ButtonBack=tk.Button(self.window,text="<<",font=self.fontTextLong,command=self.back).grid(row=4,column=0) #back
        self.window.bind('<Return>', self.next_step)# key event "enter" to go to next step
        self.window.bind('<Escape>', self.exit_process)#ke event "Esc" to exit process

        #include photo with respect to display resolution
        #resolution is stored in w, h
        if self.process_step in ['splash']: # No scaling for splash-screen
            size = self.w, self.h
            print("*********SPLASH**********")
        else:
            size = scale_factor*self.w, scale_factor*self.h

        outfile = os.path.splitext(self.image)[0] + "_" + str(int(scale_factor*self.h)) + "_thumbnail.gif"
        if not os.path.exists(outfile):
            try:
                im = Image.open(self.image)
                im.thumbnail(size, Image.ANTIALIAS)
                im.save(outfile, "GIF")
            except IOError:
                print('cannot create thumbnail for ')
                print(r'%s' %self.image)

        self.image = outfile
        self.photo=tk.PhotoImage(file= r'%s' %self.image)
        self.photo_label=tk.Label(self.window,image=self.photo)

        if self.Id not in [401,402,301,5001,598,599,7001]: #Steps without Image
            self.photo_label.grid(row=0,rowspan=5,column=2,columnspan=2,sticky=E, padx=5, pady=5)

        # Button that describes what the switch press does, does not actually get pressed
        if self.Id in (401, 502, 5001, 598, 7001):
            self.bt_text = 'Bestätigen'
            tk.Button(self.window, text = self.bt_text).grid(row = 2, column = 2)
        elif self.Id in (301, 599):
            self.bt_text = 'Weiter'
            tk.Button(self.window, text = self.bt_text).grid(row = 2, column = 2)
        else:
            if self.Id in (5030, 503, 508): # tare 504 und 509 nicht drin, da beim Wasser abwiegen mit dem Button weitergeschaltet wird (hier sollte auch kein Tare nötig sein)
                self.bt_text = 'Tarieren'
            else:
                self.bt_text = 'Weiter'
            tk.Button(self.window, text = self.bt_text).grid(row = 4, column = 3)

        if self.Id in (401, 5001, 598, 599, 7001): # steps top and bottom label (e.g. choice or simple display steps)
            self.window.configure(background = 'white')
            self.window.grid_columnconfigure(2, minsize=480)
            self.window.grid_rowconfigure(0, minsize=100)
            self.window.grid_rowconfigure(1, minsize=110)
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

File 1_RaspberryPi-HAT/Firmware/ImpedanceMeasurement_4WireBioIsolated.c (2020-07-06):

/*********************************************************************************

Copyright (c) 2013-2014 Analog Devices, Inc. All Rights Reserved.

This software is proprietary to Analog Devices, Inc. and its licensors.  By using 
this software you agree to the terms of the associated Analog Devices Software 
License Agreement.

*********************************************************************************/


/*****************************************************************************
 * @file:    ImpedanceMeasurement_4Wire.c
 * @brief:   Impedance measurement example for ADuCM350 in 4-wire configuration
 *           Bio-Impedance measurement. The ADuCM350 4Wire Bio Config Board is
 *           is required in this example
 * @version: $Revision: 29403 $
 * @date:    $Date: 2015-01-08 10:34:56 -0500 (Thu, 08 Jan 2015) $
 *****************************************************************************/

#include <stdio.h>
#include "arm_math.h"

#include "test_common.h"

#include "afe.h"
#include "afe_lib.h"
#include "uart.h"

/* Macro to enable the returning of AFE data using the UART */
/*      1 = return AFE data on UART                         */
/*      0 = return AFE data on SW (Std Output)              */
#define USE_UART_FOR_DATA           (1)

/* Excitation frequency in Hz */
#define FREQ                        (25000)
/* Peak voltage in mV */
#define VPEAK                       (599)
/* RCAL value in Ohms */
#define RCAL                        (1000)
/* RTIA value in Ohms */
//#define RTIA                        (33000)
#define RTIA                        (1000) //Change made by Citizensensor

/* Instrumentation Amplifier Gain */
#define INST_AMP_GAIN               (1.494)

/* FCW = FREQ * 2^26 / 16e6 */
#define FCW                         ((uint32_t)(((uint64_t)FREQ << 26) / 16000000 + 0.5))

/* DAC LSB size in mV = (1.6V / (2^12 - 1)) */
#define DAC_LSB_SIZE                (0.39072)

/* Sine amplitude in DAC codes */
#define SINE_AMPLITUDE              ((uint16_t)((VPEAK) / DAC_LSB_SIZE + 0.5))

/* If both real and imaginary result are within the interval (DFT_RESULTS_OPEN_MIN_THR, DFT_RESULTS_OPEN_MAX_THR),  */
/* it is considered an open circuit and results for both magnitude and phase will be 0.                             */
#define DFT_RESULTS_OPEN_MAX_THR    (1)
#define DFT_RESULTS_OPEN_MIN_THR    (-1)

/* The number of results expected from the DFT; 4 for 2 complex results */
#define DFT_RESULTS_COUNT           (4)

/* Fractional LSB size for the fixed32_t type defined below, used for printing only. */
#define FIXED32_LSB_SIZE            (625)
//#define MSG_MAXLEN                  (50)
#define MSG_MAXLEN                  (64) //Change made by Citizensensor

/* Helper macro for printing strings to UART or Std. Output */
#define PRINT(s)                    test_print(s)
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

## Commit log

2019-10-30 added connector board rev 2.0
    [RaspiConnectorBoard.kicad_pcb, RaspiConnectorBoard.sch]
2019-10-30 added enclosure stl files rev 2.0
    [CS_v2.0_Base.stl, CS_v2.0_Knob.stl, CS_v2.0_Mixer_Boden.stl, CS_v2.0_Mixer_MotorHalter.stl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]
2020-01-27 added pi software v200127
    [steps.csv]
2020-02-16 Add GPIO Connector Board overview, BOM and instructions to documentation #13
2020-02-19 added enclosure STEP files
    [cap.step, enclosure.step, knob.step]
2020-02-24 added GerberFiles
    [CS-PreAmp V1.0.GBL, CS-PreAmp V1.0.GBP, CS-PreAmp V1.0.GBS, CS-PreAmp V1.0.GTL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]
2020-02-24 added qr code for düngebroschüre and added reset of HAT
    [steps.csv]
2020-03-02 Added nitrate electrode
2020-03-02 added URL to datasheet of Nitrate electrode
2020-03-05 Changed cup amount to 5
    ISA, Calibration stock solution, calibration 4 ppm, calibration 100 ppm, sample solution
2020-03-06 added cup_cap to 6_Accessories
    [cup cap.step, cup_cap.stl]
2020-03-06 fixed hole dia
    [cup_cap.step, cup_cap.stl]
2020-05-02 Added Eagle files
    [CS-HAT V2.brd, CS-HAT V2.sch]
2020-05-02 Add BOM
    [CS-HAT V2.csv]
2020-08-03 CS Orbital Shaker Initial Commit
    [CitizenSensor_OrbitalShaker_Base.stl, CitizenSensor_OrbitalShaker_Disc.stl, CitizenSensor_OrbitalShaker_Top.stl]
2020-10-21 Added assembly Wiki pages.
2020-12-17 added fusion source files for enclosure
    [cap v7.f3d, enclosure v64.f3z, knob v5.f3d]
2022-02-15 changed some steps
    [steps.csv]
